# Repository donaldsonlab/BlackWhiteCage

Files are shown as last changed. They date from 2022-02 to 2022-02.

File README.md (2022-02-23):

# BlackWhiteCage

This repository contains 3D models, created in Solidworks, and fabrication files for designing and constructing a Black and White Cage. This is divided into two
sections: one white with an open top and the other black and enclosed. The lid for the enclosed half integrates magnets for quick and quiet attachment and removal during 
experiments. For modularity, the rest of the cage is assembled using 3D printed brackets.

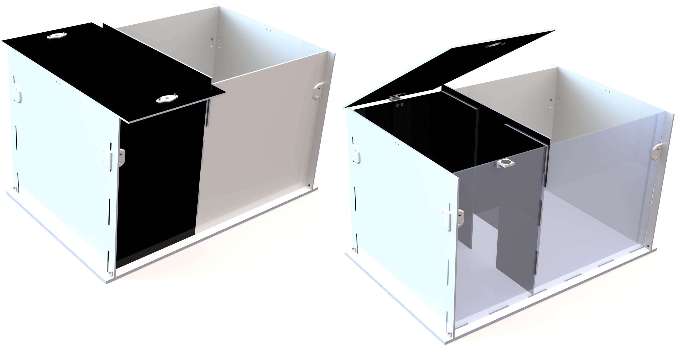
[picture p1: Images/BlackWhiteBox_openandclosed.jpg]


The walls of this chamber are laser cut out of clear 0.118" acrylic sheets and the floor is cut out of 0.22" acrylic for stability. They are then painted matte white and matte
black accordingly and assembled using 3D printed brackets. These brackets, along with the necessary fasteners, may be ommited if an adhesive
is used instead, making the assembly permanent. This is the method used for the [PPT](https://github.com/donaldsonlab/PPT-Chamber). The files used on the laser 
cutters are located in the [DXF](/DXF) directory. To optimize the nesting of parts on as few acrylic sheets as possible, we use an open source software called 
[Deepnest](https://deepnest.io/). The L-brackets, floor brackets, and magnet mounts are 3D printed on a Zortrax M200 Plus FDM printer with PLA, ABS, or Z-ULTRAT filament. The 
.STL files for printing are in the [STL](/STL) directory.

<p align="center">
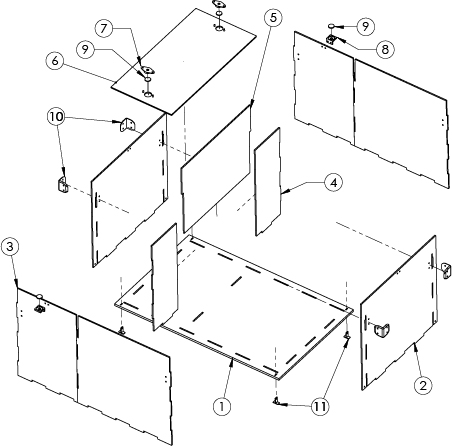
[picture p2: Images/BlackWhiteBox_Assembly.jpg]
  
</p>

|       Bill of Materials      |
--------------------------------
|Item No.|Part|Description|Quantity|
-|----------------------|------------------------------------------------------------------------|-|
1|bw_floor             |Laser cut [bw_floor.dxf](/DXF/bw_floor.dxf)                                                         |1|
2|bw_sideWall          |Laser cut [bw_sideWall.dxf](/DXF/bw_sideWall.dxf)                                                   |2|
3|bw_frontBack         |Laser cut [bw_frontBack.dxf](/DXF/bw_frontBack.dxf)                                                 |2|
4|bw_doorway           |Laser cut [bw_doorway.dxf](/DXF/bw_doorway.dxf)                                                     |2|
5|bw_door              |Laser cut [bw_door.dxf](/DXF/bw_door.dxf)                                                           |1|
6|bw_lid               |Laser cut [bw_door.dxf](/DXF/bw_door.dxf)                                                           |1|
7|bw_magnetMount_Lid   |3D printed PLA/ABS [bw_magnetMount_Lid.stl](/STL/bw_magnetMount_Lid.stl)                            |2|
8|bw_magnetMount_Wall  |3D printed PLA/ABS [bw_magnetMount_Wall.stl](/STL/bw_magnetMount_Wall.stl)                          |2|
9|15x2mm Disk Magnets  |[Off-the-shelf 15x2mm refrigerator magnets](https://www.amazon.com/DIYMAG-Refrigerator-Magnets-Premium-Brushed/dp/B07G48647D) |4|
10|bw_LBracket         |Optional 3D printed PLA/ABS [bw_LBracket.stl](/STL/bw_LBracket.stl)                                 |4|
11|bw_floorBracket     |Optional 3D printed PLA/ABS [bw_floorBracket.stl](/STL/bw_floorBracket.stl)                         |4|
12|M3x8mm Screws       |Off-the-shelf screws required for magnet mounts but optional for brackets if using plastic cement   |16|
13|Plastic Cement      |Optional Plastruct Plastic Weld or IPS Weld-On 3 Acrylic Plastic Cement                             |<1|
14|Matte White Paint   |[Krylon Fusion All-In-One Spray Paint, Matte, White, 12 oz.](https://www.walmart.com/ip/Krylon-Fusion-All-In-One-Spray-Paint-Matte-White-12-oz/678882687)|<1|
15|Matte Black Paint   |[Black, Rust-Oleum American Accents 2X Ultra Cover Ultra Matte Spray Paint, 12 oz](https://www.walmart.com/ip/Black-Rust-Oleum-American-Accents-2X-Ultra-Cover-Ultra-Matte-Spray-Paint-12-oz/488512581)|<1|

The brand of acrylic cement is not important, as long as it can hold the acrylic pieces together. Similarly, the brand of paint is unimportant and can either be *matte* or 
*flat*, although matte finishes can typically withstand more cleaning. The magnets can also be sourced elsewhere, but the mounts are fitted for 15x2mm disk magnets.

**Note:** If the wall 
thickness is adjusted, the 3D models and .DXF files must also be modified. This can be done manually in the part files or by using the text file, 
[blackWhiteEquations.txt](blackWhiteEquations.txt), which contains equations used for each Solidworks part. Simply change the "WallThickness" and/or "FloorThickness" to the 
desired value and rebuild or refresh the part file.

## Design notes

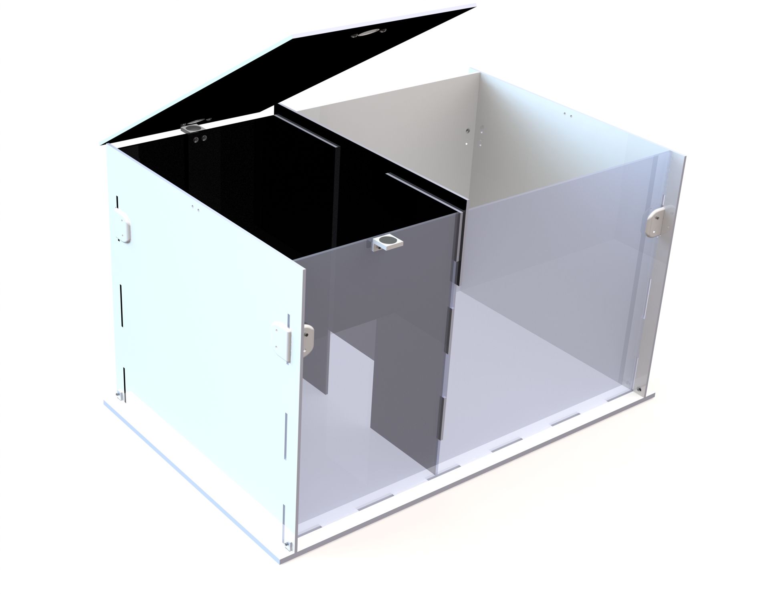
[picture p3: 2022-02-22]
Images/BlackWhiteBox_open.JPG

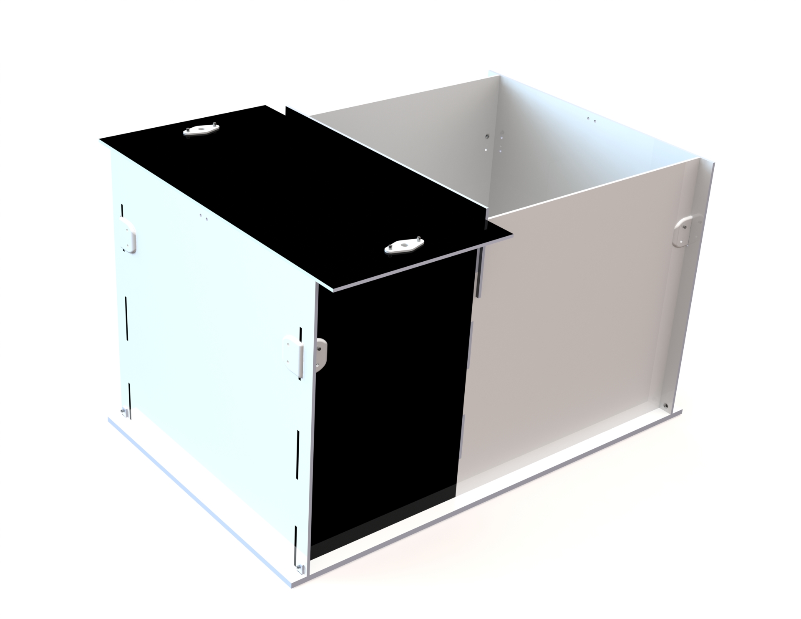
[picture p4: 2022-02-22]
Images/BlackWhiteBox.JPG

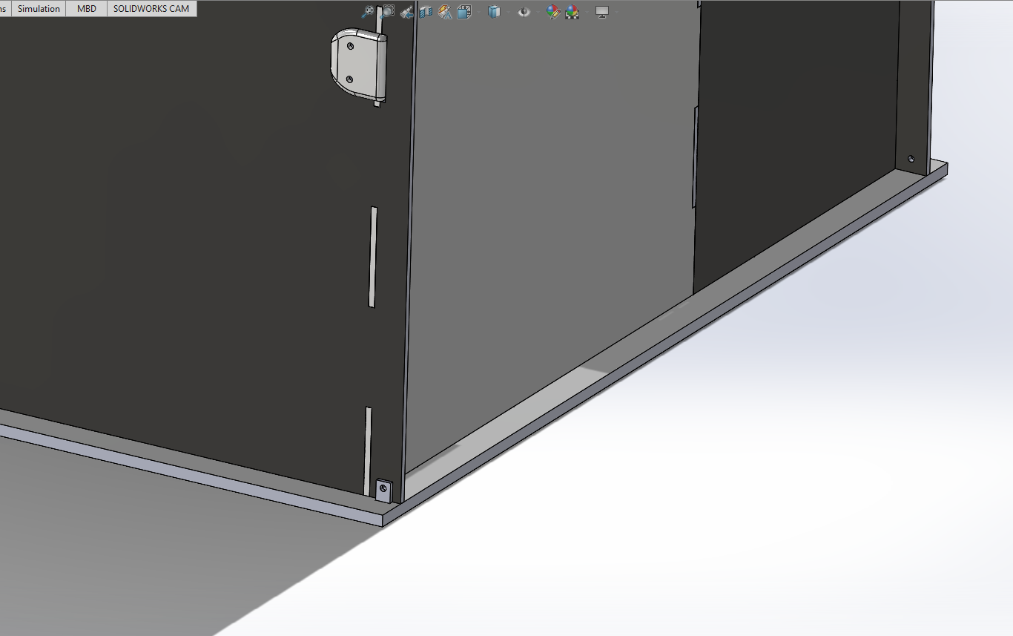
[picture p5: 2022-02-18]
Images/bw_withOverhang.png

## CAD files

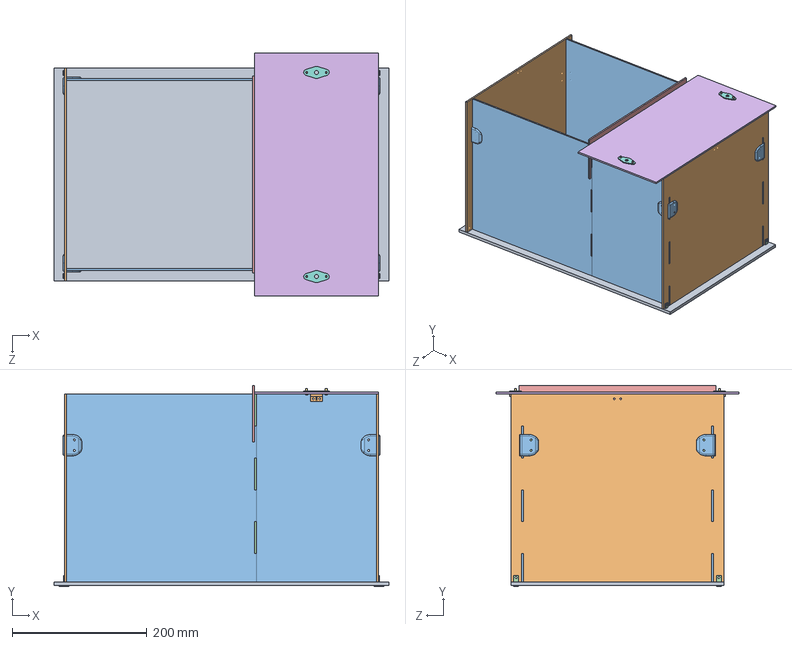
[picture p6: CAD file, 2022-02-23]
BlackWhiteBox_Assembly.SLDASM
497.9 x 299.2 x 361.6 mm
bw_floor
bw_sideWall x 2
bw_frontBack x 2
bw_doorway x 2
bw_door
bw_lid
socket button head cap screw_am x 4
bw_magnetMount_Lid x 2
magnet_disc_15x2 x 4
bw_magnetMount_Wall x 2
bw_LBracket x 4
bw_floorBracket x 4

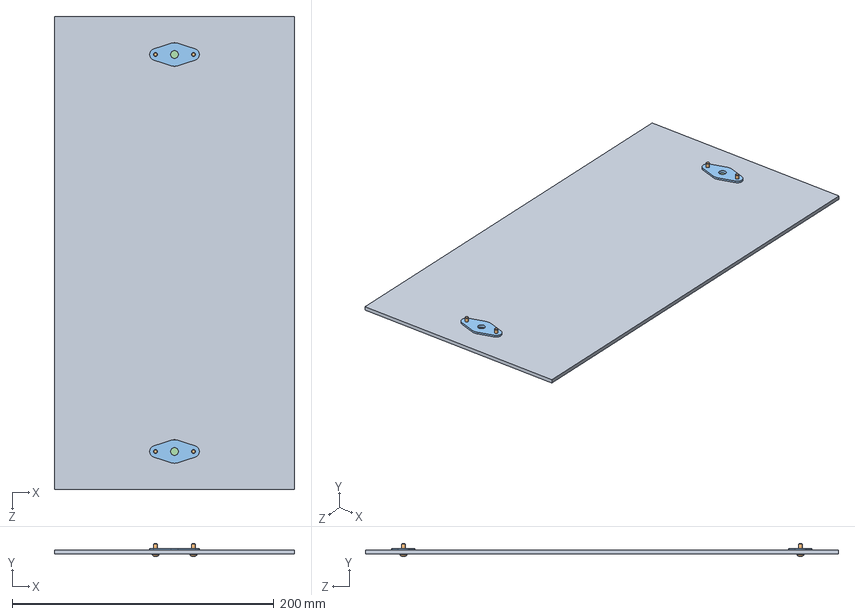
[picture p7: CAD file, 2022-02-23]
bw_lid_assembly.SLDASM
183.8 x 9.65 x 361.6 mm
bw_lid
socket button head cap screw_am x 4
bw_magnetMount_Lid x 2
magnet_disc_15x2 x 2

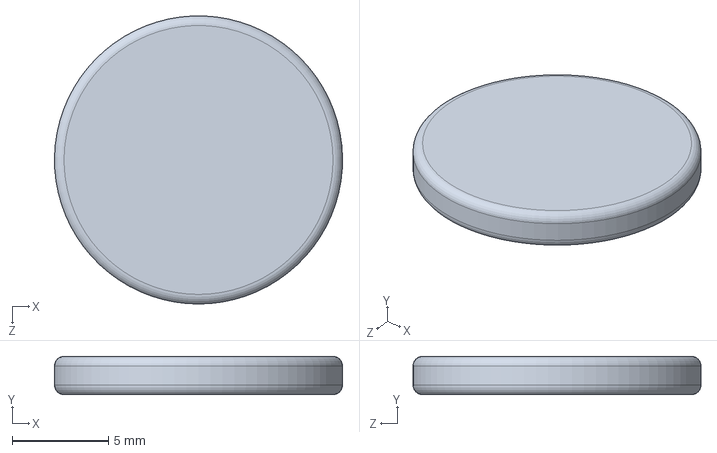
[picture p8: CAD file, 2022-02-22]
bw_magnetMount_Lid_Assembly.SLDASM
15.0 x 2.00 x 15.0 mm

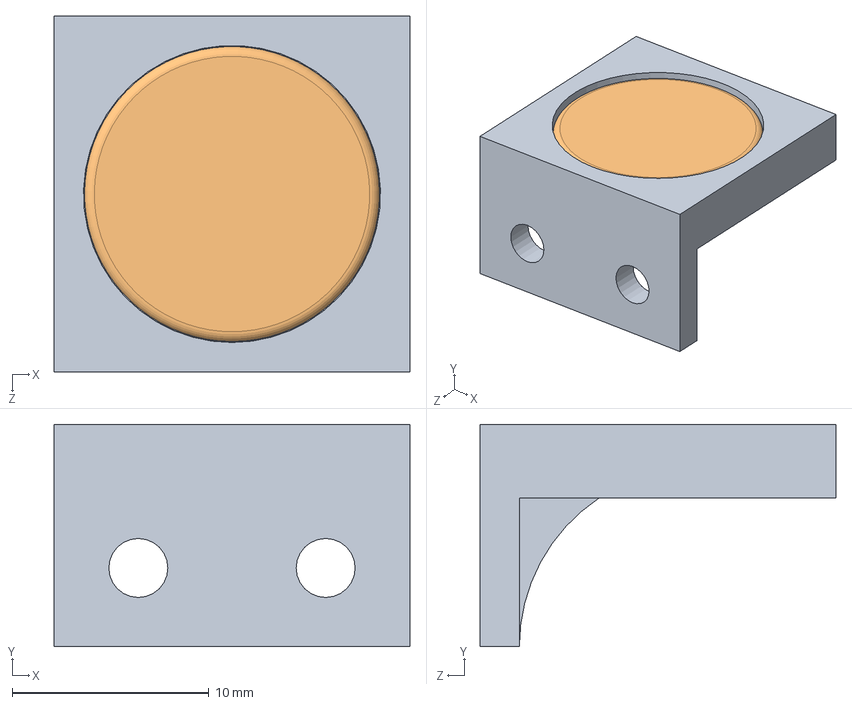
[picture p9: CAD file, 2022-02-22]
bw_magnetMount_Wall_Assembly.SLDASM
18.1 x 11.3 x 18.1 mm
bw_magnetMount_Wall
magnet_disc_15x2

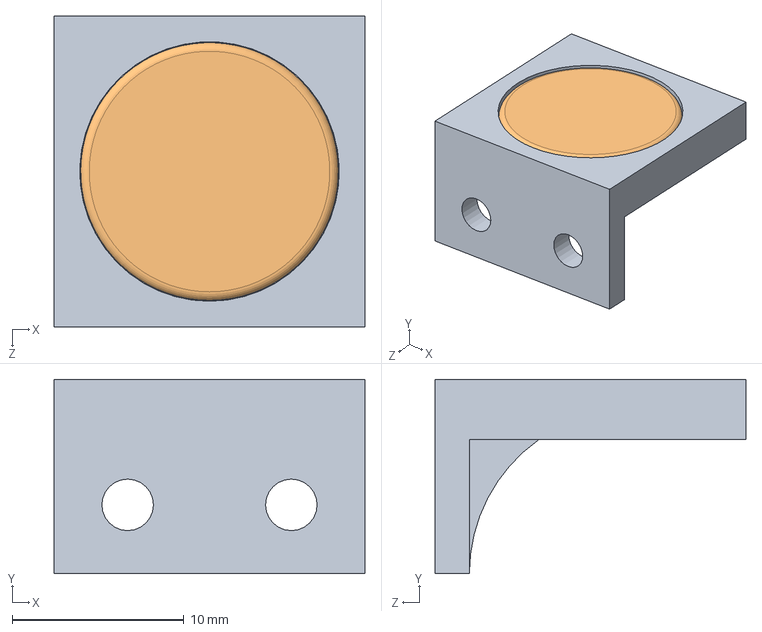
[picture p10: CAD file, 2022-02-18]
bw_magnetWallMount_assembly.SLDASM
18.1 x 11.3 x 18.1 mm
bw_magnetWallMount
magnet_disc_15x2

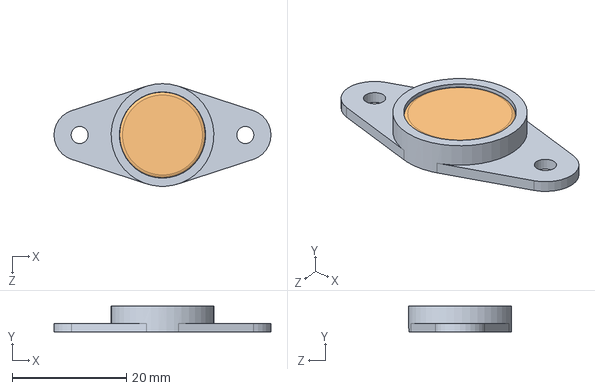
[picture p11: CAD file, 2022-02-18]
bw_magnetTopMount_assembly.SLDASM
38.0 x 4.50 x 18.0 mm
bw_magnetTopMount
magnet_disc_15x2

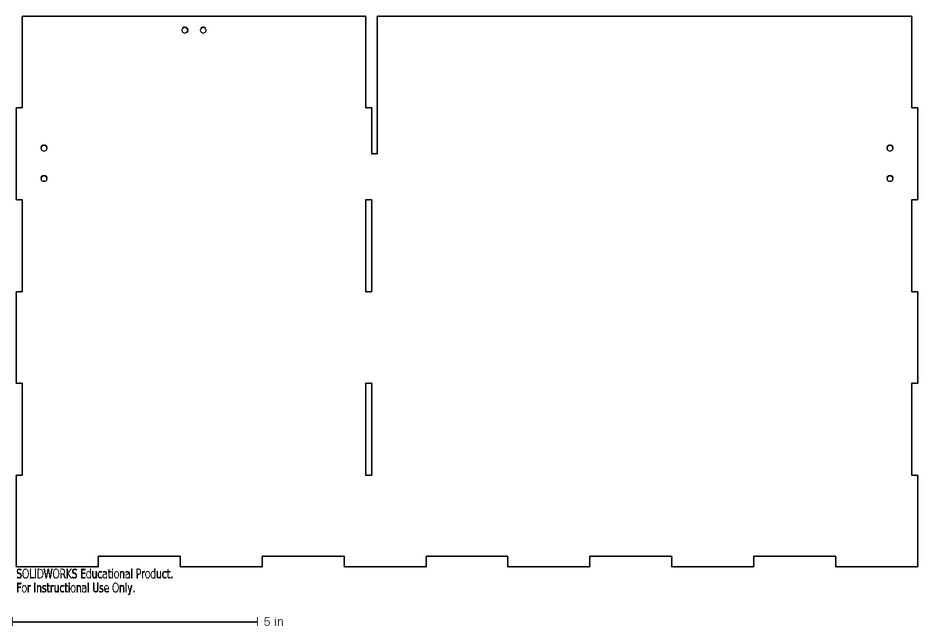
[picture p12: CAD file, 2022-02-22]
Laser Cutting/bw_frontBack.DXF
SOLIDWORKS Educational Product.
For Instructional Use Only.

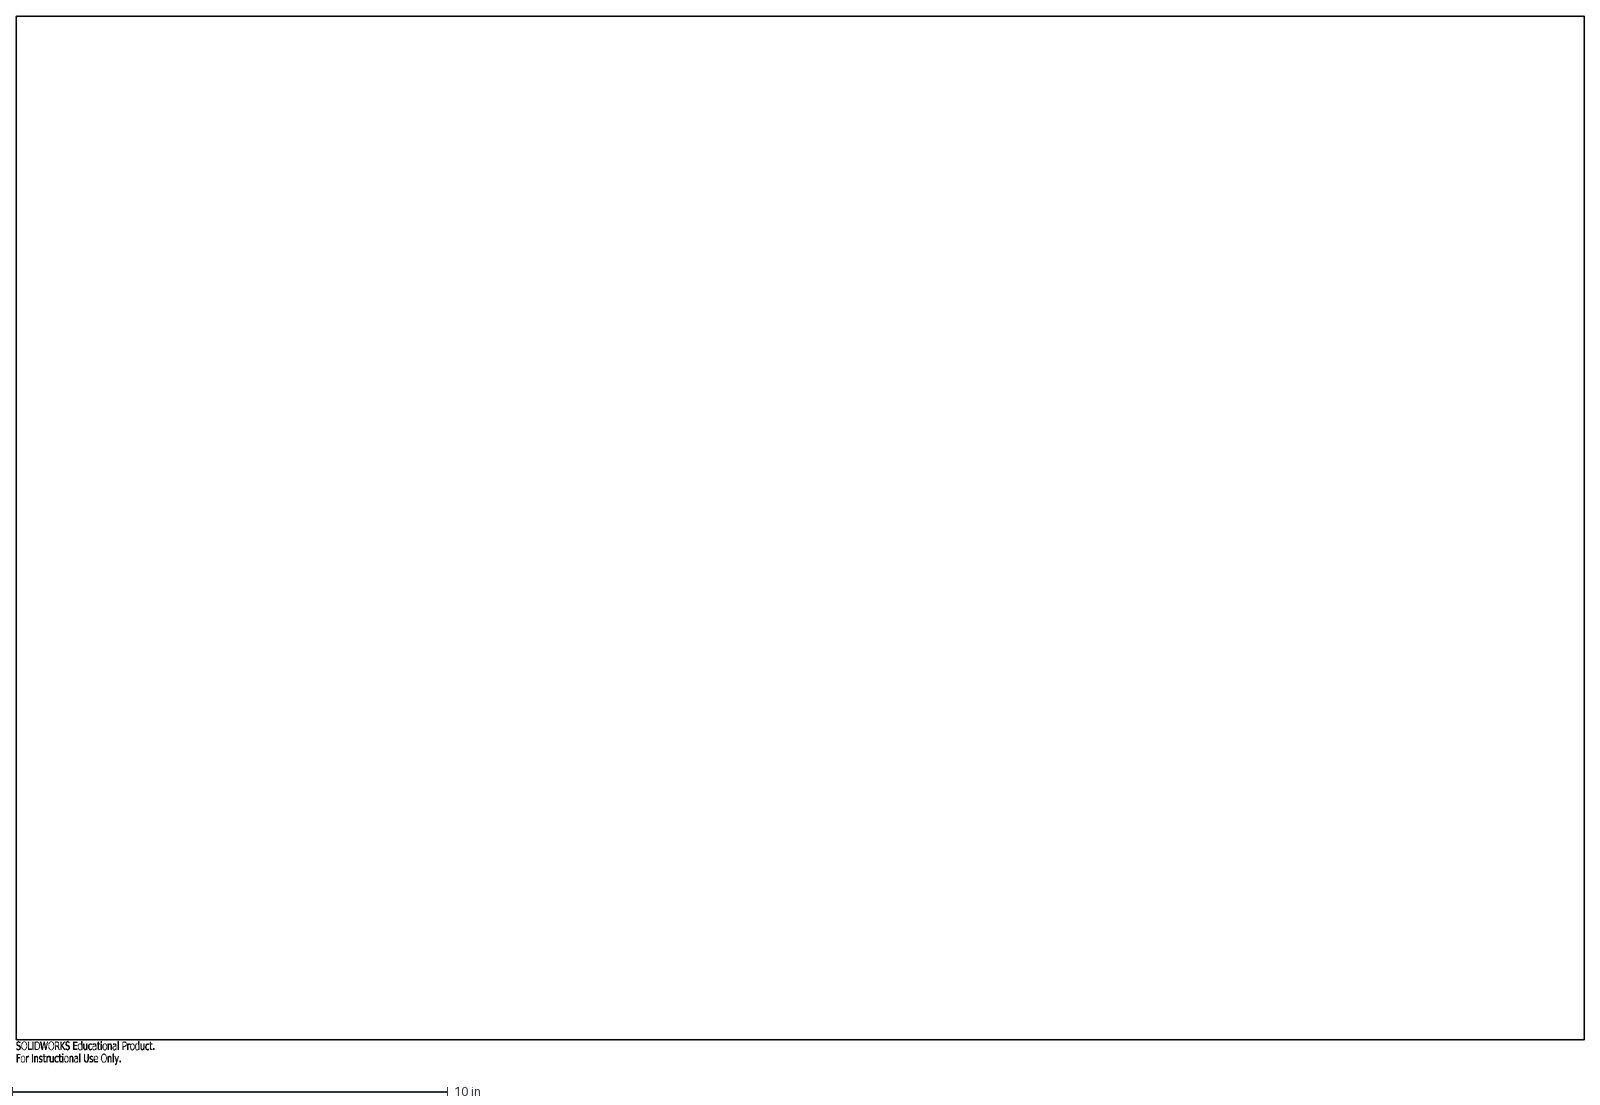
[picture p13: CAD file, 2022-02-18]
Laser Cutting/BoundingBox_24x36.DXF
SOLIDWORKS Educational Product.
For Instructional Use Only.

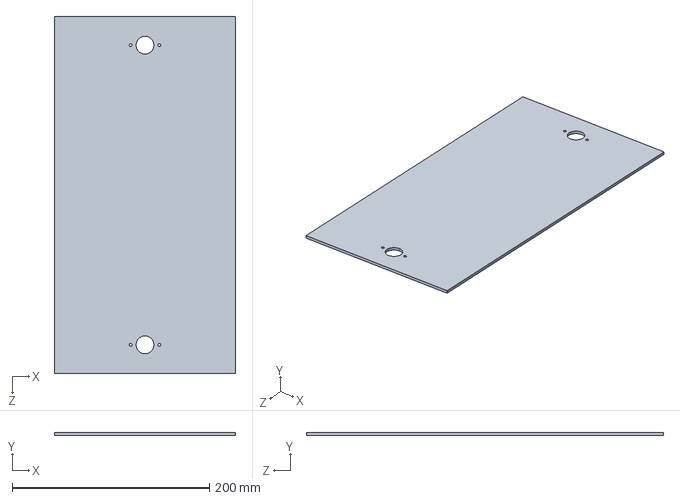
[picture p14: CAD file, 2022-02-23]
bw_lid.SLDPRT
183.8 x 3.00 x 361.6 mm

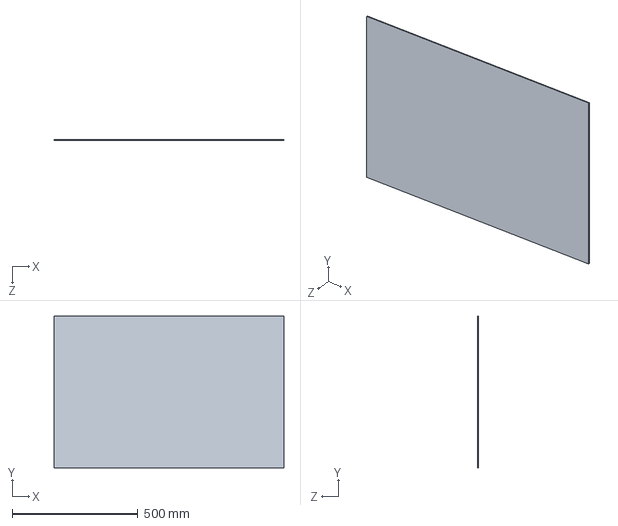
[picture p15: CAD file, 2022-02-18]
Laser Cutting/BoundingBox.SLDPRT
914.4 x 603.2 x 3.17 mm

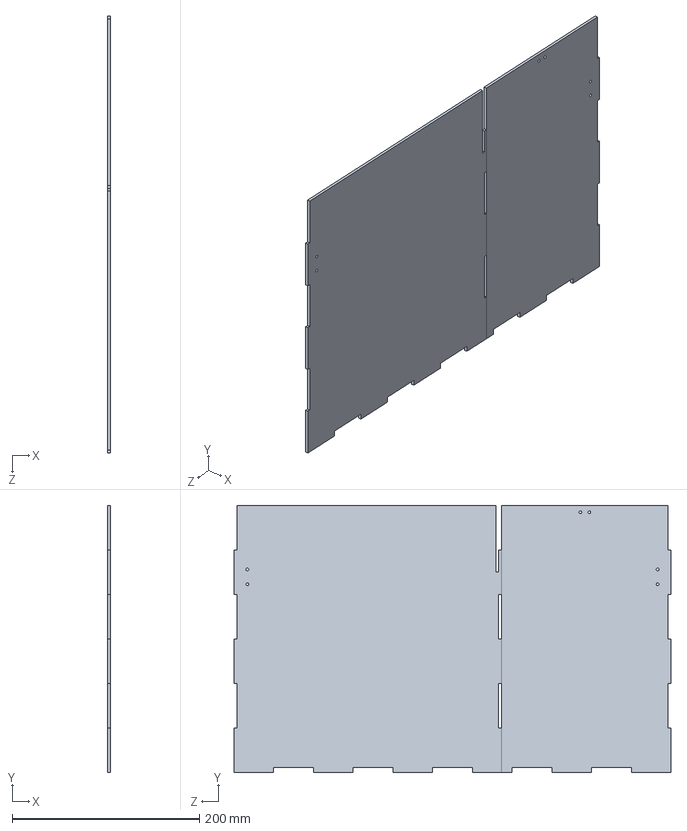
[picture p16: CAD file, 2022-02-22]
bw_frontBack.SLDPRT
3.00 x 285.0 x 466.2 mm

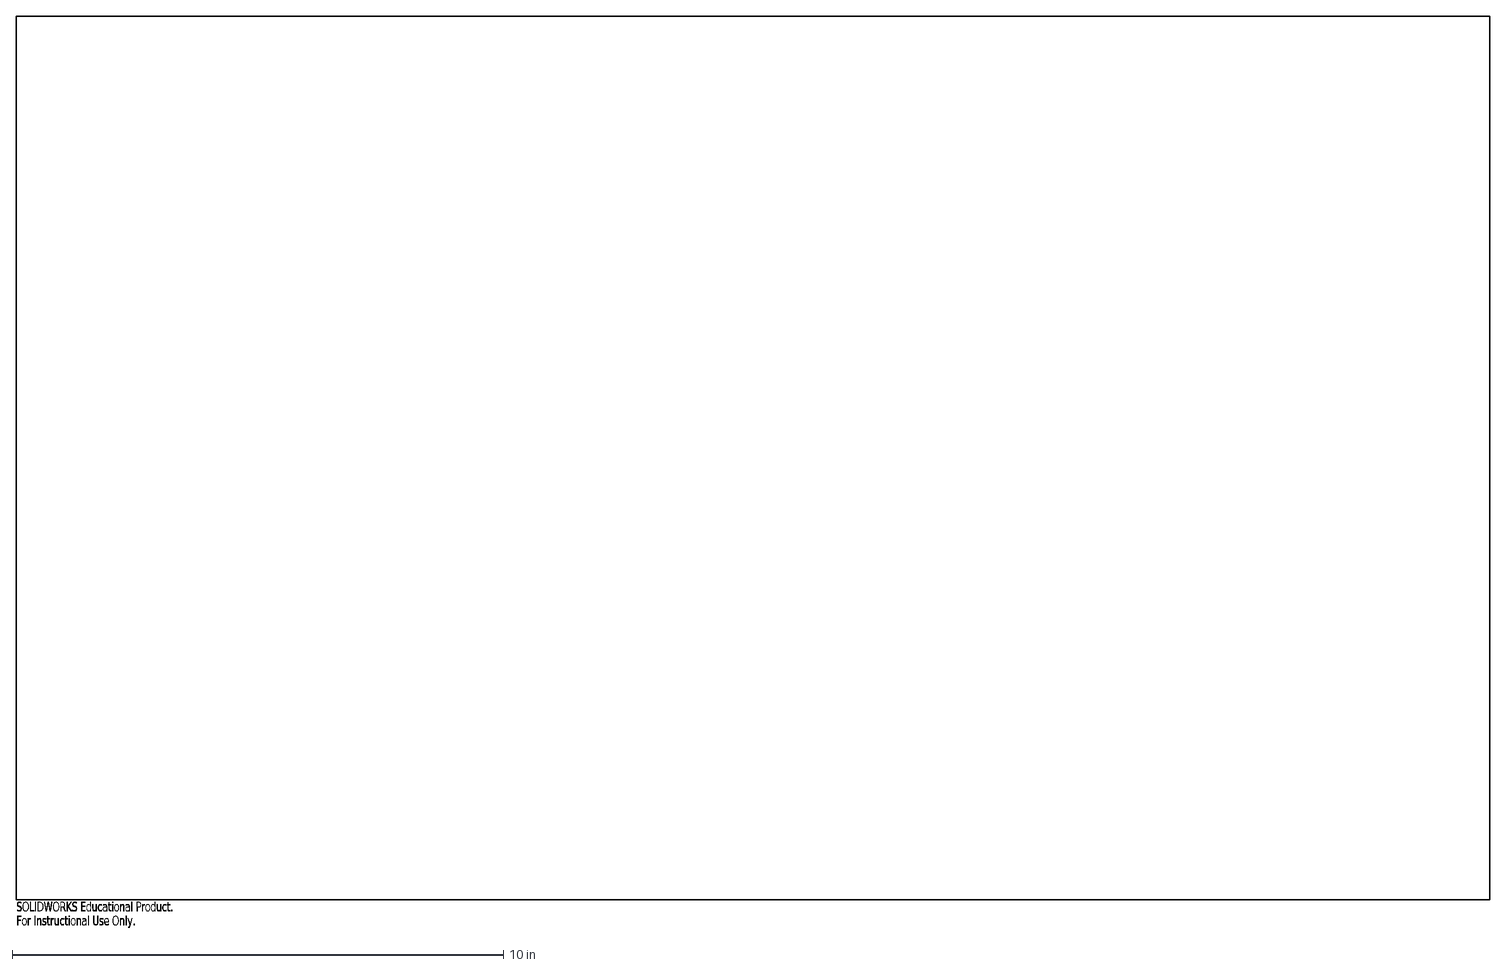
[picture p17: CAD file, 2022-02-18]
Laser Cutting/BoundingBox_18x30.DXF
SOLIDWORKS Educational Product.
For Instructional Use Only.

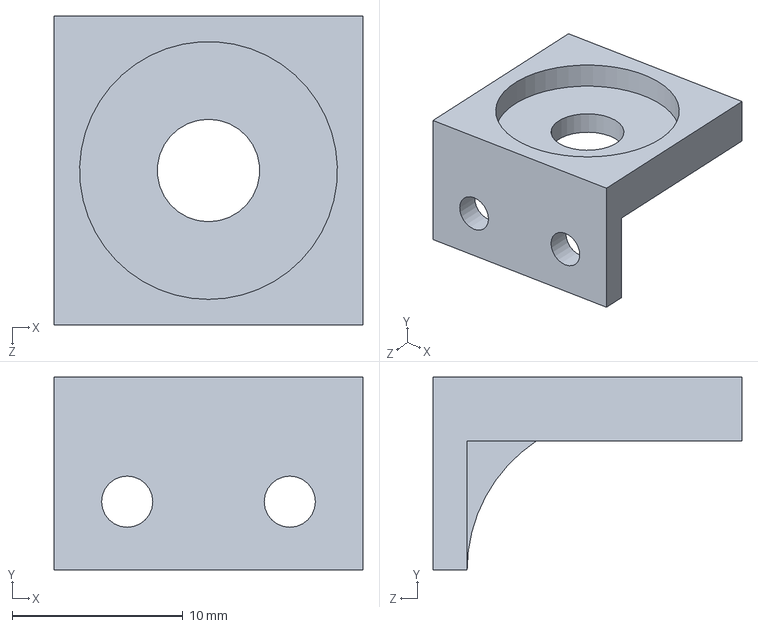
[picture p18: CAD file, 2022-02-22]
bw_magnetMount_Wall.SLDPRT
18.1 x 11.3 x 18.1 mm

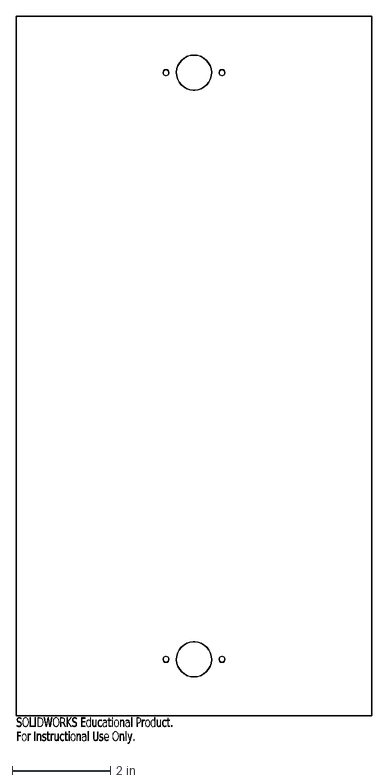
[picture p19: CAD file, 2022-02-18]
Laser Cutting/bw_blackLid.DXF
SOLIDWORKS Educational Product.
For Instructional Use Only.

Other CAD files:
Laser Cutting/BoundingBox_24x30.DXF
bw_LBracket.SLDPRT
Laser Cutting/BoundingBox_25x10_5.DXF
bw_doorway.SLDPRT
Alternate Lid Mount/bw_screw.SLDPRT
Alternate Lid Mount/bw_screwMount.SLDPRT
BlackWhiteBox_Assembly.SLDDRW
Laser Cutting/BoundingBox.DXF
Laser Cutting/BoundingBox_12x30.DXF
Laser Cutting/BoundingBox_12x36.DXF
Laser Cutting/BoundingBox_15x30.DXF
Laser Cutting/BoundingBox_16x13_5.DXF
Laser Cutting/bw_door.DXF
Laser Cutting/bw_doorway.DXF
Laser Cutting/bw_floor.DXF
Laser Cutting/bw_side.DXF
STL/bw_LBracket.STL
STL/bw_feet.STL
STL/bw_floorBracket.STL
STL/bw_magnetMount_Lid.STL
STL/bw_magnetMount_Wall.STL
STL/bw_magnetTopMount.STL
STL/bw_magnetWallMount.STL
STL/bw_screw.STL
STL/bw_screwMount.STL
bw_blackLid.SLDPRT
bw_door.SLDPRT
bw_feet.SLDPRT
bw_floor.SLDPRT
bw_floorBracket.SLDPRT
bw_magnetMount_Lid.SLDPRT
bw_magnetTopMount.SLDPRT
bw_magnetWallMount.SLDPRT
bw_sideWall.SLDPRT
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

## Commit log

2022-02-18 Initial release
    [BlackWhiteBox_Assembly.SLDASM, BoundingBox.DXF, BoundingBox.SLDPRT, BoundingBox_12x30.DXF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]
2022-02-22 Updated images
    [BlackWhiteBox_Assembly.SLDASM, bw_LBracket.SLDPRT, bw_LBracket.STL, bw_door.SLDPRT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]
2022-02-23 Add Assembly Picture
    [BlackWhiteBox_Assembly.SLDASM, BlackWhiteBox_Assembly.SLDDRW, bw_lid.SLDPRT, bw_lid_assembly.SLDASM]
